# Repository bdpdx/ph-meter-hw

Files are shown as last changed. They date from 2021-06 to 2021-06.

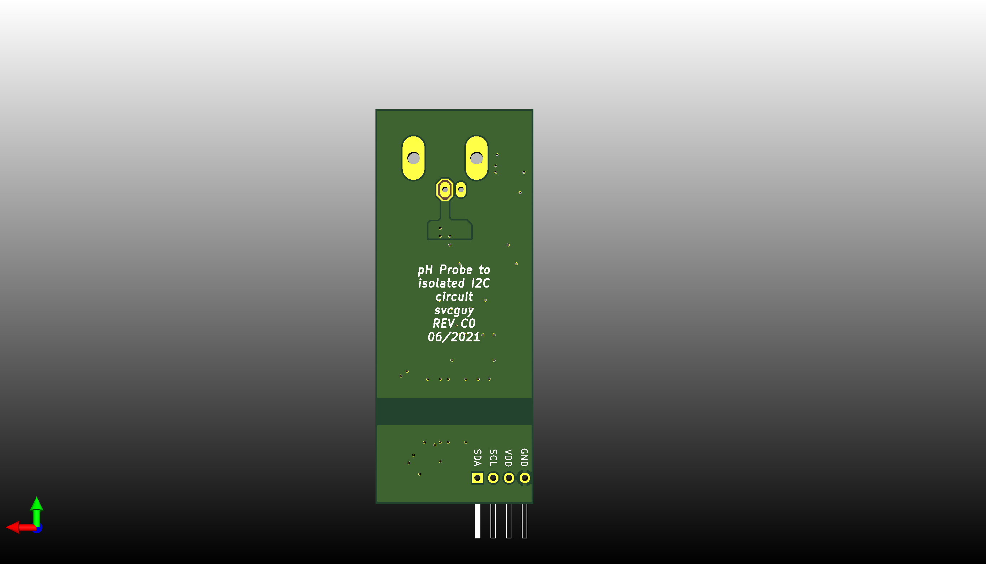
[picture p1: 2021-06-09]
doc/phMeter_bot.png

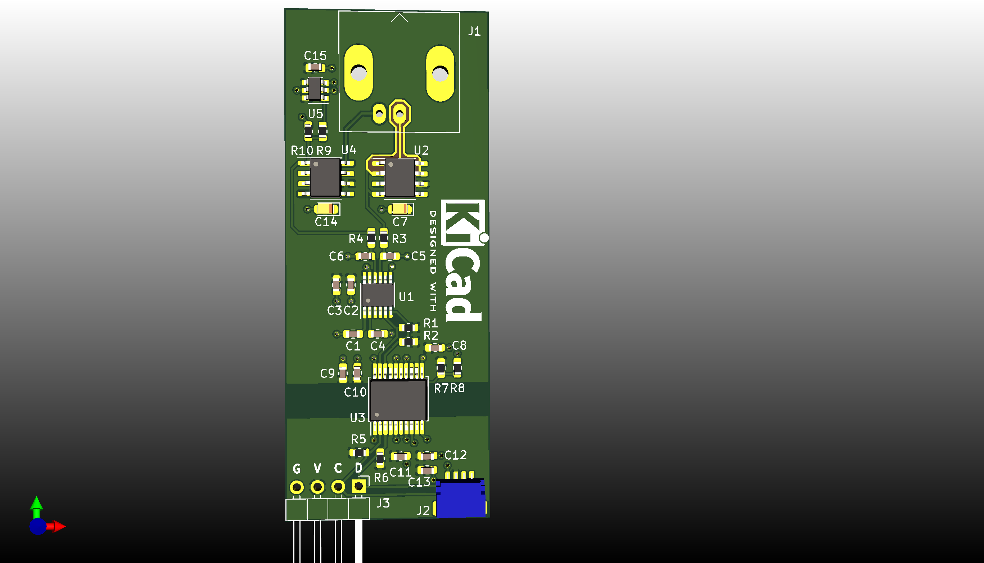
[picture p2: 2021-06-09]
doc/phMeter_top.png

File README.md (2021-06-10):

# phMeter
## A simple combination pH probe interface circuit

This is a simple analog front end (AFE), ADC and I2C isolator circuit to interface to a standard combination pH electrode.

## Circuit Theory of Operation
### AFE
A standard combination pH probe has the following electrial characteristics
- Very high output impedance (100MOhm - 1GOhm)
- Bipolar sub 1V output voltage (+/- 400mV)

The first characteristic requires careful circuit design.  First we must convert that high output impedance to a much lower one for input into an ADC.  U2, a LMP7721 opamp does this for us.  Next the really high output impedance has issues with leakage current.  Because the current drawn from the sensor is in the 100s of pA range, any current lost to leakage will have a significant effect on the reading from the sensor.  To combat leakage current, guard rings around and below the high impedance traces are employed.  The LMP7721 is specifically designed for this using a special pinout that allows easy implementation of a guard ring.  As well as using low leakage tanalum capacitors for supply bypassing on the opamp.  The pA range currents also require careful selection of the opamp.  The TI LMP7721 choosen is used because of its fA range input bias currents.  Most opamps with pA or even uA input bias currents will completely destroy or at best significantly affect the probe readings.
The second characteristic isn't as much of an issue.  One could use an ADC that is bipolar (positive and negative supplied) and directly read the negative output voltage of the sensor.  However, generating the negative supply requires more circuitry and more importantly often times injects a large source of noise into the system.  Another approach, the one used here, is to bias (shift) the sensor output up enough so that the sensor output never swings negative.  U4 (another LMP7721) is used to bias the reference electrode up by +512mV.  Often the reference electrode is connected to GND, but by doing this the sensor will give an output of ~100mV-900mV.  The voltage required to bias the sensor is generated by U5, a MCP1501 1.024V reference voltage source.  The output of U5 is passed to a voltage divider to obtain 512mV.  Which leads to the ...
### ADC
Dividing the reference voltage using a resistor divider introduces error as well.  The tolerances and thermal coeffecients of the resistors will lead to error in this new "reference" voltage which is biased into the sensor output voltage.  To remove these errors, a differential ADC is used.  U1, a LTC2473, is a 16bit sigma-delta differential input ADC with I2C output.  For the LTC2473, a ~1kOhm input resistance is recommended as well as a 0.1uF input capacitor.  The LTC2473 has a internally generated reference voltage of 1.25V.  With an input voltage range from the sensor of 0.1V to 0.9V, most all of the range of the ADC is utilized.
### I2C Isolation
We want galvanic isolation between the sensor and the rest of the system. This reduces the noise injected into the system as well as this system interferring with any other (potential) systems measuring the same sample, or vice versa.  The ADM3260, U3, provides an isolated power supply, ground and I2C bus drivers for this application.  The resistor divider of R7 and R8 sets the output voltage of the isolated DC-DC converter, in this case the output voltage is set to 3.3V to match the input voltage.

## Performance
*COMING SOON*

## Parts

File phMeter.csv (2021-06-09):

Reference | Quantity | Value | Footprint | Datasheet | Digikey
C15 | 1 | 2.2uF | jlcpcb_smt:C_0603_1608Metric | ~ | 445-6933-1-ND
C3 C9 C13 | 3 | 10uF | jlcpcb_smt:C_0603_1608Metric | ~ | 445-9065-1-ND
C1 C2 C4 C5 C6 C8 C10 C11 C12 | 9 | 0.1uF | jlcpcb_smt:C_0603_1608Metric | ~ | 311-1088-1-ND
C7 C14 | 2 | 0.1uF | Capacitor_Tantalum_SMD:CP_EIA-2012-15_AVX-P | https://datasheets.avx.com/TAJ_LOW_PROFILE.pdf | 478-11592-1-ND
J1 | 1 | PH_PROBE | Connector_Coaxial:BNC_Amphenol_B6252HB-NPP3G-50_Horizontal | https://s3-us-west-2.amazonaws.com/catsy.582/C031-71052.pdf | ARF2869-ND
J2 | 1 | QWIIC | Custom_KICAD:QWIIC_STEMMA_QT | https://www.jst-mfg.com/product/pdf/eng/eSH.pdf | 455-1804-1-ND
J3 | 1 | I2C | Connector_PinHeader_2.54mm:PinHeader_1x04_P2.54mm_Horizontal | ~ | DNP
R1 R2 R5 R6 | 4 | 4.7k | jlcpcb_smt:R_0603_1608Metric | ~ | RMCF0603FT4K70CT-ND
R3 R4 | 2 | 1k | jlcpcb_smt:R_0603_1608Metric | ~ | P1.00KHCT-ND
R7 | 1 | 16.9k | jlcpcb_smt:R_0603_1608Metric | ~ | P16.9KHCT-ND
R8 R9 R10 | 3 | 10k | jlcpcb_smt:R_0603_1608Metric | ~ | P10.0KHCT-ND
U1 | 1 | LTC2473 | Package_SO:MSOP-12_3x4mm_P0.65mm | https://www.analog.com/media/en/technical-documentation/data-sheets/24713fb.pdf | LTC2473CMS#PBF-ND
U3 | 1 | ADM3260 | Package_SO:SSOP-20_5.3x7.2mm_P0.65mm | https://www.analog.com/media/en/technical-documentation/data-sheets/adm3260.pdf | ADM3260ARSZ-RL7CT-ND
U2 U4 | 2 | LMP7721 | Package_SO:SOIC-8_3.9x4.9mm_P1.27mm | https://www.ti.com/lit/ds/symlink/lmp7721.pdf | LMP7721MA/NOPB-ND
U5 | 1 | MCP1501 | Package_TO_SOT_SMD:SOT-23-6 | https://ww1.microchip.com/downloads/en/DeviceDoc/20005474E.pdf | MCP1501T-10E/CHYCT-ND

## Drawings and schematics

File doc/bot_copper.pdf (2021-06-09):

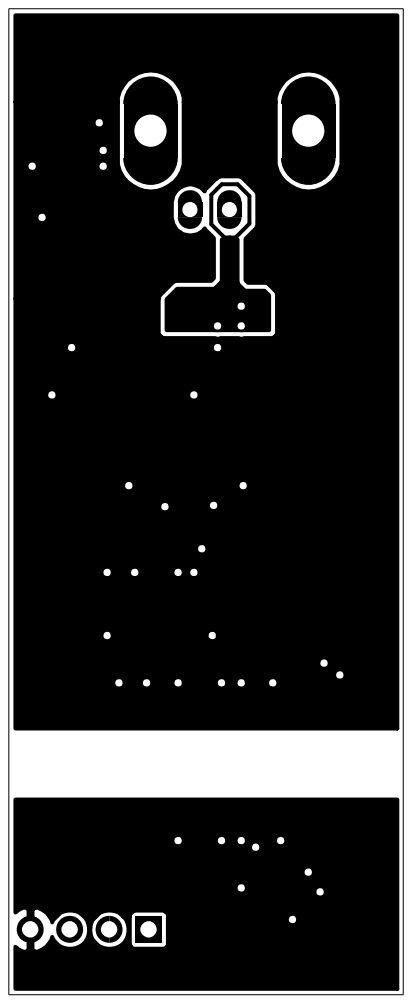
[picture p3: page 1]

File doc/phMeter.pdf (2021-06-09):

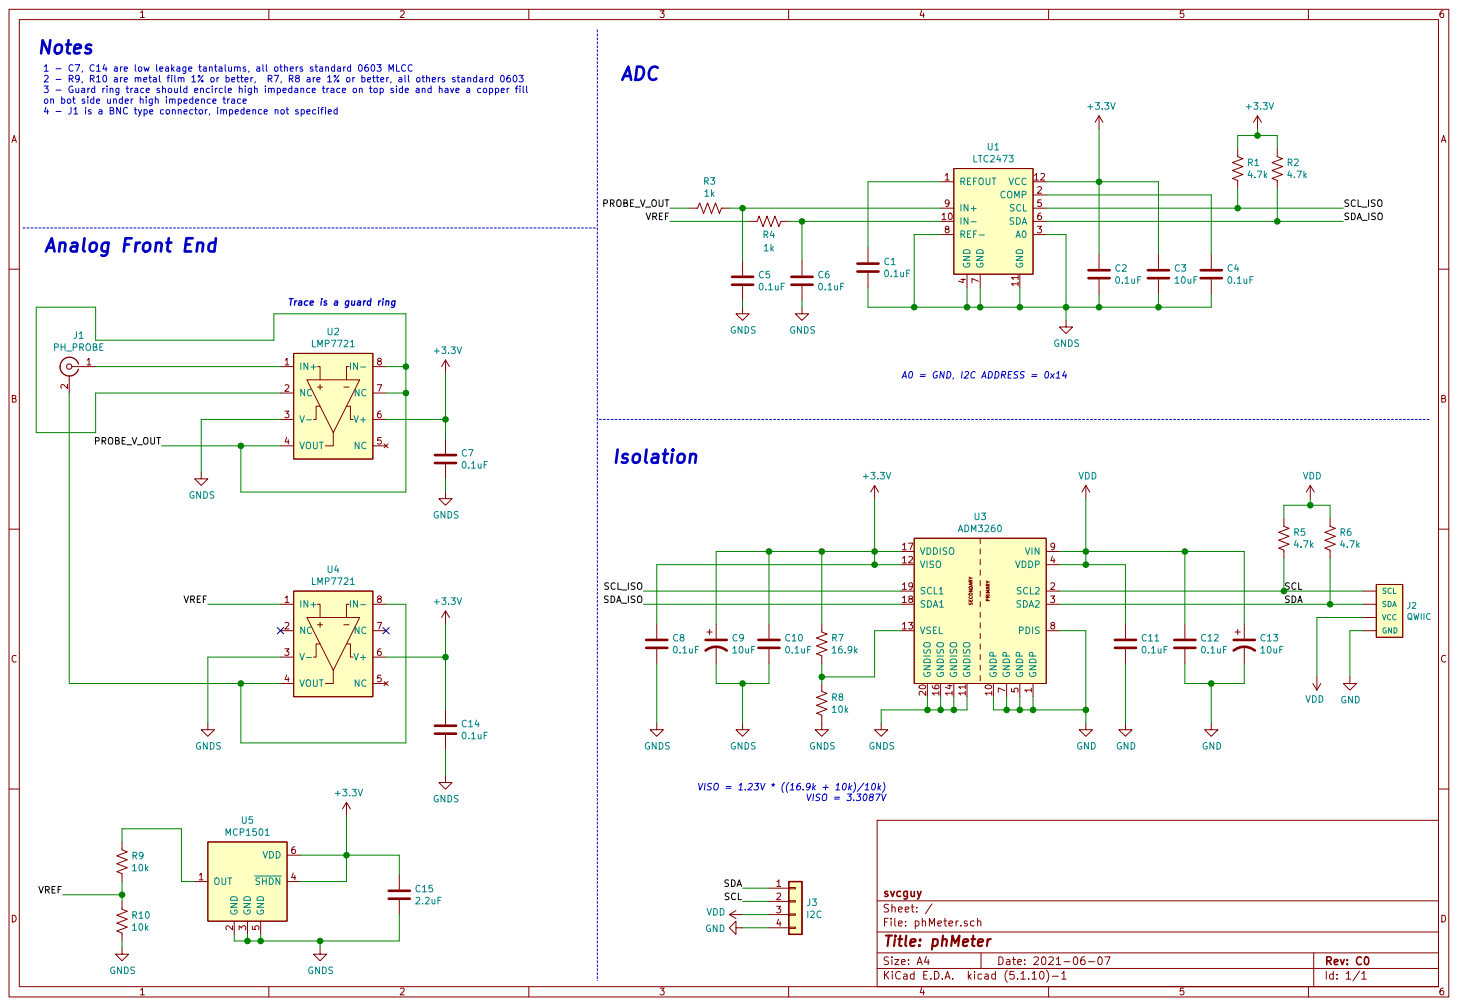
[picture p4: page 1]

1 - C7, C14 are low leakage tantalums, all others standard 0603 MLCC
2 - R9, R10 are metal film 1% or better, R7, R8 are 1% or better, all others standard 0603
3 - Guard ring trace should encircle high impedance trace on top side and have a copper fill
on bot side under high impedence trace
4 - J1 is a BNC type connector, impedence not specified

move C5, C6 closer to LTC2473, Add LTC2473 I2C address note Trace is a guard ring

A0 = GND, I2C ADDRESS = 0x14 Analog Front End

1 GNDP 10 GNDISO 11 VISO 12 VSEL 13 GNDISO 14 GNDISO 16 VDDISO 17 SDA1 18 SCL1 19 SCL2 2 GNDISO 20 SDA2 3 VDDP 4 GNDP

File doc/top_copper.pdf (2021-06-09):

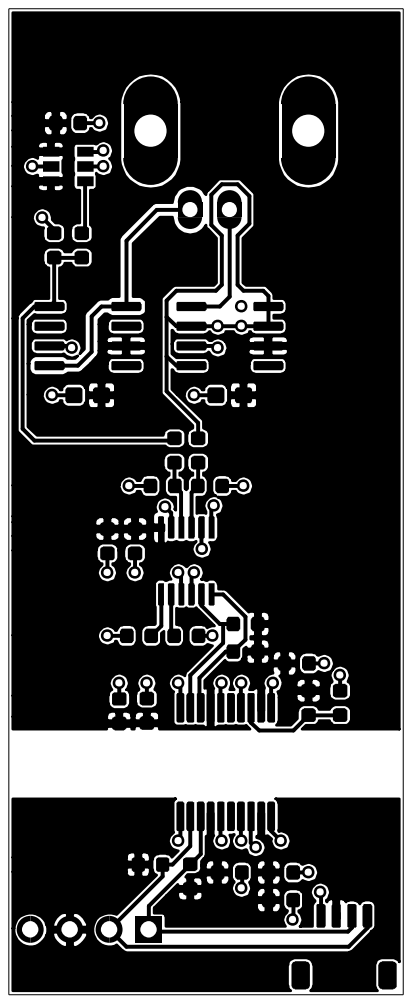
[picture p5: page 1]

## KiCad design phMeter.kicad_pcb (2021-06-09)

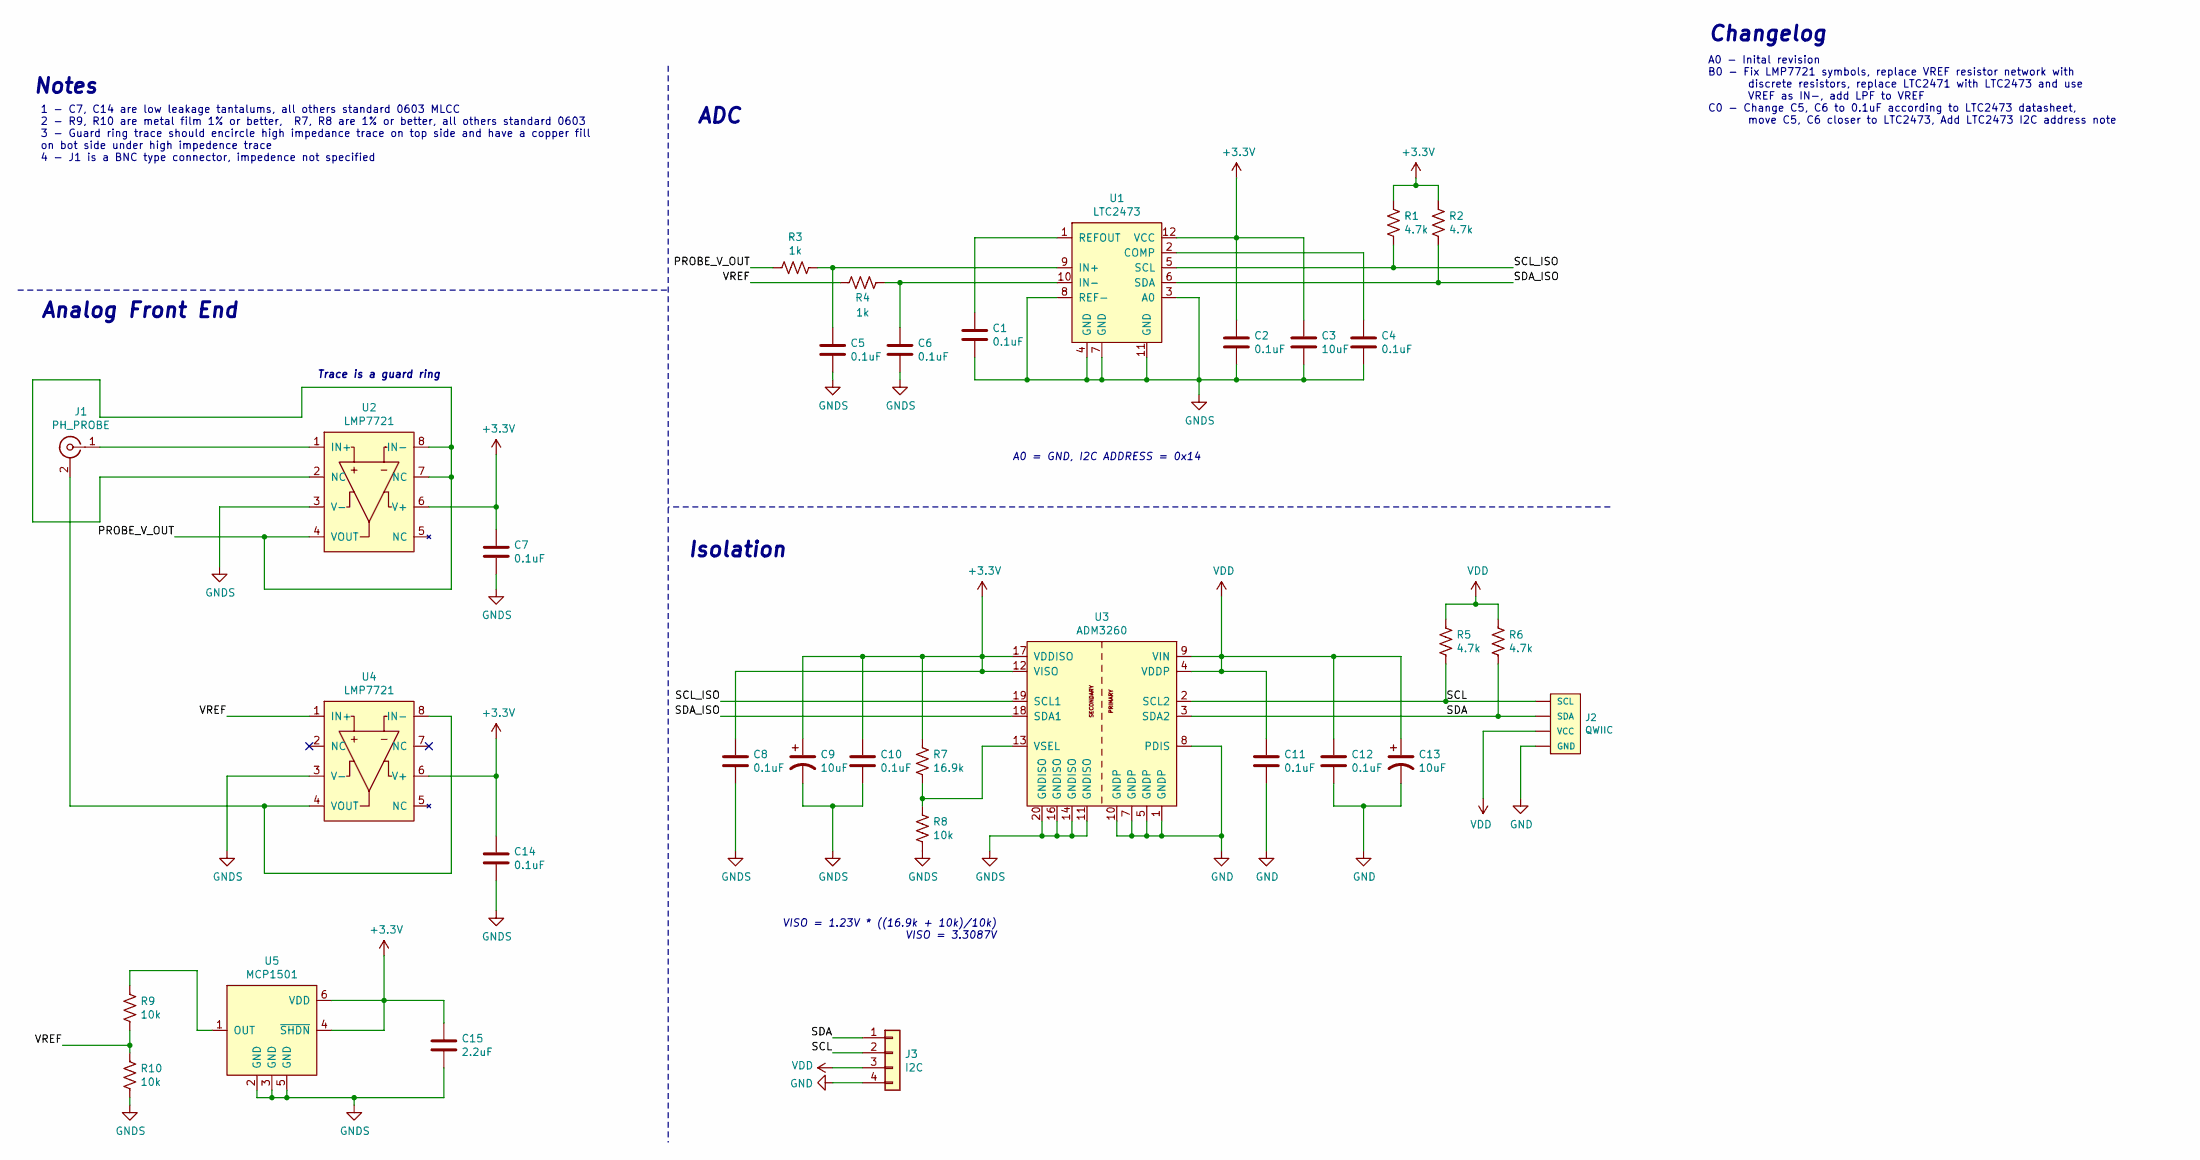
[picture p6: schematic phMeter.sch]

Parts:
C1, C2, C4, C5, C6, C8, C10, C11, C12: 0.1uF; C_0603_1608Metric; Digikey 311-1088-1-ND
C3, C9, C13: 10uF; C_0603_1608Metric; Digikey 445-9065-1-ND
C7, C14: 0.1uF; CP_EIA-2012-15_AVX-P; Digikey 478-11592-1-ND
C15: 2.2uF; C_0603_1608Metric; Digikey 445-6933-1-ND
J1: PH_PROBE; BNC_Amphenol_B6252HB-NPP3G-50_Horizontal; Digikey ARF2869-ND
J2: QWIIC; QWIIC_STEMMA_QT; Digikey 455-1804-1-ND
J3: I2C; PinHeader_1x04_P2.54mm_Horizontal; Digikey DNP
R1, R2, R5, R6: 4.7k; R_0603_1608Metric; Digikey RMCF0603FT4K70CT-ND
R3, R4: 1k; R_0603_1608Metric; Digikey P1.00KHCT-ND
R7: 16.9k; R_0603_1608Metric; Digikey P16.9KHCT-ND
R8: 10k; R_0603_1608Metric; Digikey P10.0KHCT-ND
R9, R10: 10k; R_0603_1608Metric; Digikey 2019-RN73H1JTTD1002F100CT-ND
U1: LTC2473; MSOP-12_3x4mm_P0.65mm; Digikey LTC2473CMS#PBF-ND
U2, U4: LMP7721; SOIC-8_3.9x4.9mm_P1.27mm; Digikey LMP7721MA/NOPB-ND
U3: ADM3260; SSOP-20_5.3x7.2mm_P0.65mm; Digikey ADM3260ARSZ-RL7CT-ND
U5: MCP1501; SOT-23-6; Digikey MCP1501T-10E/CHYCT-ND

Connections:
+3V3: C2.1, C3.1, C7.1, C8.1, C9.1, C10.1, C14.1, C15.1, R1.1, R2.1, R7.1, U1.12 (VCC), U2.6 (V+), U3.12 (VISO), U3.17 (VDDISO), U4.6 (V+), U5.4 (~SHDN), U5.6 (VDD)
/PROBE_V_OUT: R3.2, U2.2 (NC), U2.4 (VOUT), U2.7 (NC), U2.8 (IN-)
/SCL: J2.4 (SCL), J3.2, R5.2, U3.2 (SCL2)
/SCL_ISO: R1.2, U1.5 (SCL), U3.19 (SCL1)
/SDA: J2.3 (SDA), J3.1, R6.2, U3.3 (SDA2)
/SDA_ISO: R2.2, U1.6 (SDA), U3.18 (SDA1)
/VREF: R4.2, R9.2, R10.1, U4.1 (IN+)
GND: C11.2, C12.2, C13.2, J2.1 (GND), J3.4, U3.1 (GNDP), U3.5 (GNDP), U3.7 (GNDP), U3.8 (PDIS), U3.10 (GNDP)
GNDS: C1.2, C2.2, C3.2, C4.2, C5.2, C6.2, C7.2, C8.2, C9.2, C10.2, C14.2, C15.2, R8.2, R10.2, U1.3 (A0), U1.4 (GND), U1.7 (GND), U1.8 (REF-), U1.11 (GND), U2.3 (V-), U3.11 (GNDISO), U3.14 (GNDISO), U3.16 (GNDISO), U3.20 (GNDISO), U4.3 (V-), U5.2 (GND), U5.3 (GND), U5.5 (GND)
unnamed: C1.1, U1.1 (REFOUT)
unnamed: C4.1, U1.2 (COMP)
unnamed: C5.1, R3.1, U1.9 (IN+)
unnamed: C6.1, R4.1, U1.10 (IN-)
unnamed: J1.1 (In), U2.1 (IN+)
unnamed: J1.2 (Ext), U4.4 (VOUT), U4.8 (IN-)
unnamed: R7.2, R8.1, U3.13 (VSEL)
unnamed: R9.1, U5.1 (OUT)
VDD: C11.1, C12.1, C13.1, J2.2 (VCC), J3.3, R5.1, R6.1, U3.4 (VDDP), U3.9 (VIN)

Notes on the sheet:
Trace is a guard ring
VISO = 1.23V * ((16.9k + 10k)/10k) VISO = 3.3087V
Analog Front End
ADC
Isolation
Notes
1 - C7, C14 are low leakage tantalums, all others standard 0603 MLCC 2 - R9, R10 are metal film 1% or better, R7, R8 are 1% or better, all others standard 0603 3 - Guard ring trace should encircle high impedance trace on top side and have a copper fill on bot side under high impedence trace 4 - J1 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
A0 - Inital revision B0 - Fix LMP7721 symbols, replace VREF resistor network with discrete resistors, replace LTC2471 with LTC2473 and use VREF as IN-, add LPF to VREF C0 - Change C5, C6 to 0.1uF according to LTC2473 datasheet, move C5, C6 closer to LTC2473, Add LTC2473 I2C address note
Changelog
A0 = GND, I2C ADDRESS = 0x14

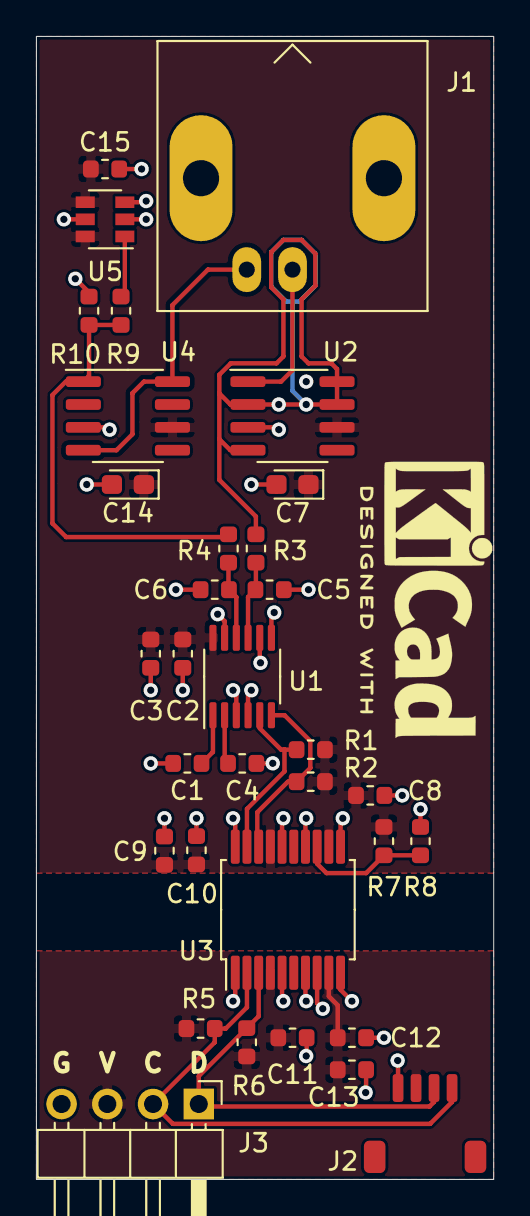
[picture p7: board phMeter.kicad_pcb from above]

Board: 2 copper layers, 25.4 x 63.5 mm, 33 parts (0 on the bottom side), 18 nets.

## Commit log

2021-06-07 REV A0
    [phMeter.kicad_pcb, phMeter.sch]
2021-06-08 SCH REV B0, PCB REV B0
    [phMeter-B_Cu.gbl, phMeter-B_Mask.gbs, phMeter-B_Paste.gbp, phMeter-B_SilkS.gbo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]
2021-06-09 SCH REV C0, PCB REV C0, added simulation files
    [phMeter-B_Cu.gbl, phMeter-B_Mask.gbs, phMeter-B_Paste.gbp, phMeter-B_SilkS.gbo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]
2021-06-10 Add README and device datasheets
